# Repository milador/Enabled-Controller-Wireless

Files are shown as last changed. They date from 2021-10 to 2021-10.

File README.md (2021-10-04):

# Enabled-Controller-Wireless
Enabled Controller Wireless is an open-source bluetooth-enabled switch interface that enables those with limited or no hand movement to be able to use Adaptive switches and analog joysticks as inputs to operate their computers, smartphones, and game consoles.

<p align="center">
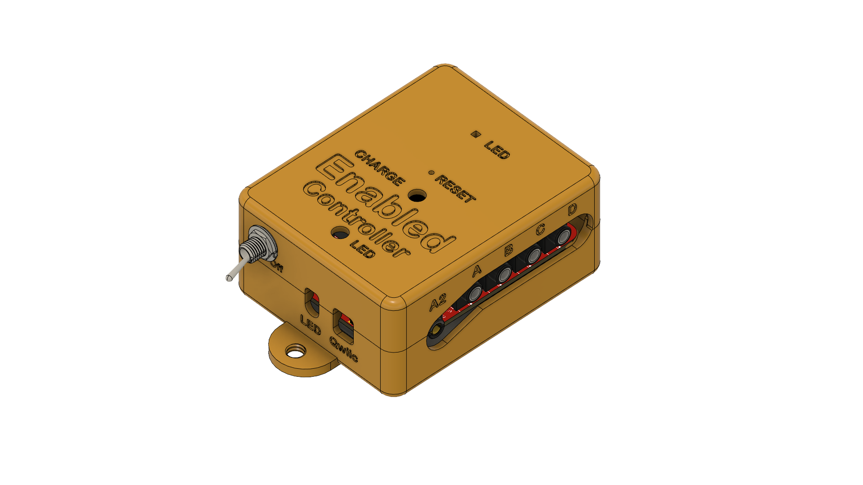
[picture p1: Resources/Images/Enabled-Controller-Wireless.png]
Enabled Controller Wireless

</p>

The device offers up to eight switch input enclosures through eight 3.5mm audio jacks and four analog inputs through two 3.5mm headphone jacks. The two 3.5mm headphone jacks can be used to connect up to two X-Y analog joysticks.

The internal RGB led of ItsyBitsy and external NeoPixel is used to provide visual feedback for each action.

## Assembly Instructions Manual

The <a href="https://github.com/milador/Enabled-Controller-Wireless/blob/master/Documentation/Build_Manuals/Enabled_Controller_Wireless_Instructions_Manual.pdf">Assembly Instructions Manual</a> is available to download.

## User Manual

### Enabled Controller Wireless User Manual

<a href="https://github.com/milador/Enabled-Controller-Wireless/blob/master/Documentation/User_Manuals/Enabled_Controller_Wireless_User_Manual.pdf">Enabled_Controller_Wireless_User_Manual.pdf</a>

## Parts

The <a href="https://github.com/milador/Enabled-Controller-Wireless/blob/master/Components/Enabled_Controller_Wireless_BOM.csv">BOM</a> file is available to download.

## Software

### Enabled_Controller_Wireless_Software.ino  

The <a href="https://raw.githubusercontent.com/milador/Enabled-Controller-Wireless/master/Software/Arduino/Enabled_Controller_Wireless_Software/Enabled_Controller_Wireless_Software.ino">Enabled_Controller_Wireless_Software.ino</a> allows you to use adaptive switches as input method via keyboard/mouse HID profiles. 

## Hardware 

### PCB Design 

The <a href="https://github.com/milador/Enabled-Controller-Wireless/tree/master/Hardware/PCB">PCB files</a> including both PCB Eagle design files and generated gerber files are available to download.

Front PCB:
<p align="center">
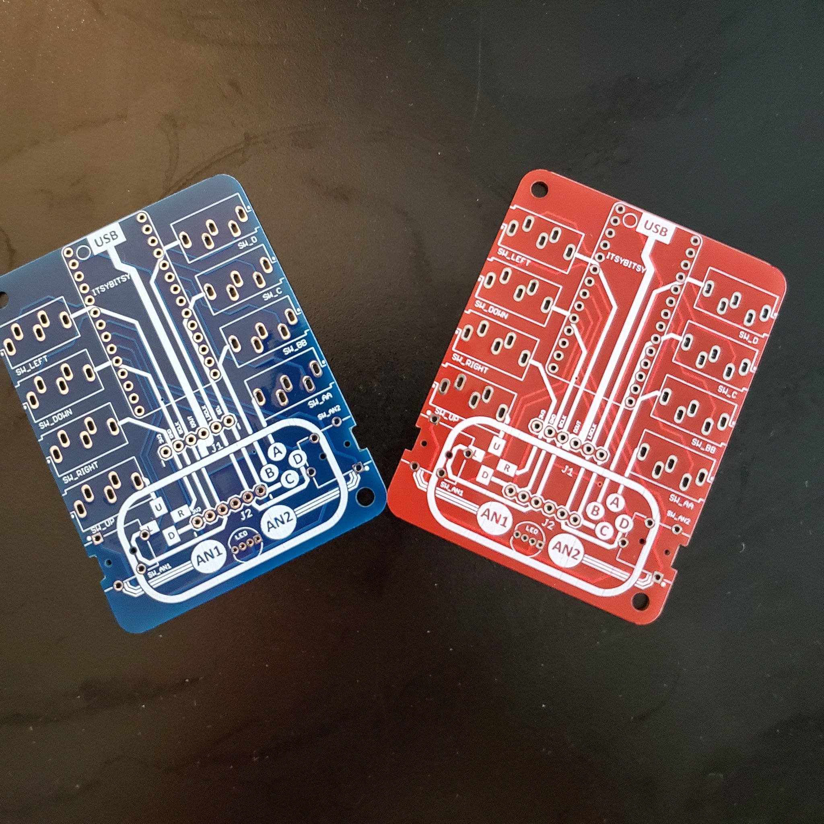
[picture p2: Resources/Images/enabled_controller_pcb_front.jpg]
Front PCB

</p>

Back PCB:
<p align="center">
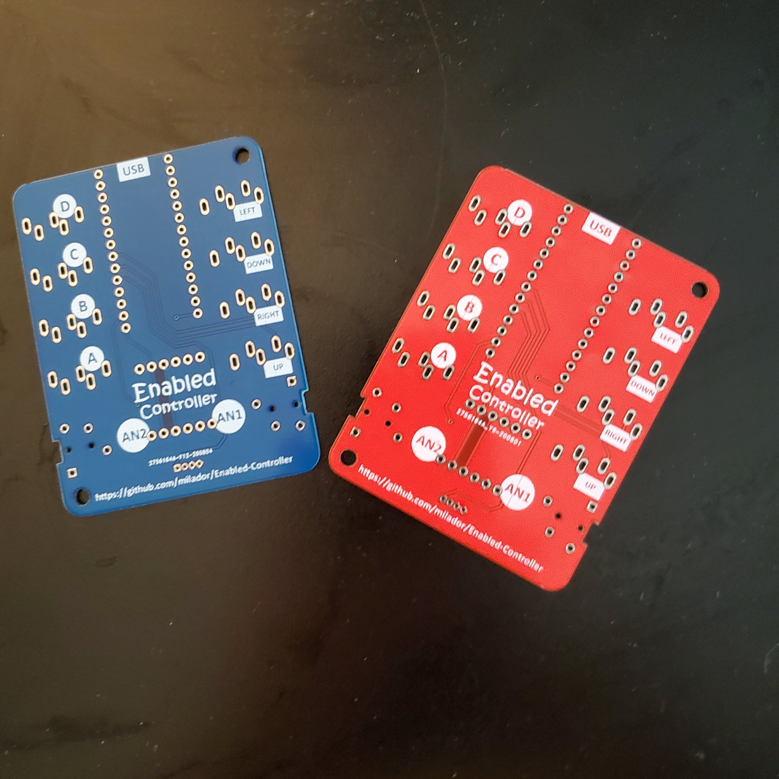
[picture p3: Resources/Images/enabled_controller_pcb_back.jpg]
Back PCB

</p>

Assembled:
<p align="center">
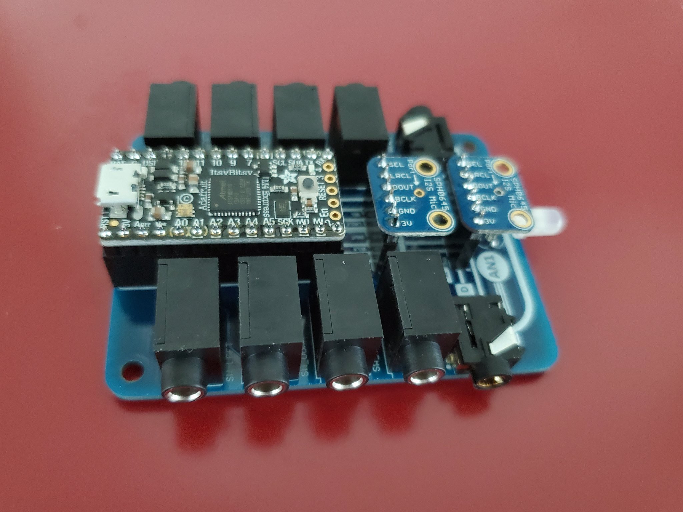
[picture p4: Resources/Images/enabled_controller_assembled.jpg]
Assembled PCB

</p>

Assembly Animation:

https://www.youtube.com/watch?v=7AMCL-cITrQ

### Enclosure

The <a href="https://github.com/milador/Enabled-Controller-Wireless/tree/master/Hardware/Enclosure">Enclosure files</a> including both STL and STEP enclosure files are available to download.

<p align="center">
Enabled Controller Wireless
</p>

## License

### Creative Commons Attribution-NonCommercial-ShareAlike (CC-BY-NC-SA)

Copyright (c) 2021 Milador

A creative commons license that bans commercial use and requires you to release any modified works under this license.

<p align="center">
CC-BY-NC-SA
</p>

<br />This work is licensed under a <a rel="license" href="http://creativecommons.org/licenses/by-nc-sa/3.0/">Creative Commons Attribution-NonCommercial-ShareAlike 3.0 Unported License</a>.

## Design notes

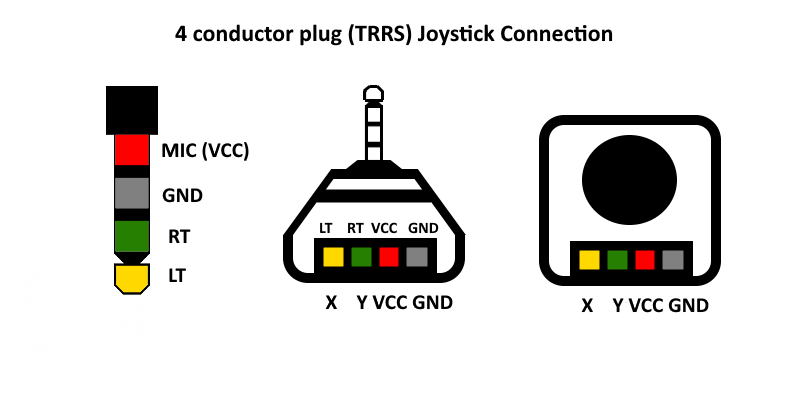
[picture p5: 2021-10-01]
Resources/Images/TRRS_Joystick_Mapping.png

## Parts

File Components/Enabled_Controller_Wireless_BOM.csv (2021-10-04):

Index | Quantity | Digikey Part Number | Manufacturer Part Number | Description | Price (CAD) | Unit Price (CAD) | Link
1 | 1 | 1528-4481-ND | 4481 | ITSYBITSY NRF52840 EXPRESS BLE | 26.96 | 26.96 | https://www.digikey.ca/en/products/detail/adafruit-industries-llc/4481/11497502
2 | 1 | 1568-1213-ND | COM-12986 | ADDRESS LED DISC SER RGB 5MM 5PC | 3.99 | 3.99 | https://www.digikey.ca/en/products/detail/COM-12986/1568-1213-ND/5673799
3 | 2 | S7047-ND | PPPC141LFBN-RC | CONN HDR 14POS 0.1 GOLD | 1.28 | 1.28 | https://www.digikey.ca/en/products/detail/PPPC141LFBN-RC/S7047-ND/810186
4 | 8 | CP1-3535NG-ND | SJ1-3535NG | CONN JACK STEREO 3.5MM R/A | 1.61 | 1.61 | https://www.digikey.ca/product-detail/en/cui-inc/SJ1-3535NG/CP1-3535NG-ND
5 | 2 | CP-43514-ND | SJ-43514 | CONN JACK 4COND 3.5MM | 1.43 | 1.43 | https://www.digikey.ca/en/products/detail/SJ-43514/CP-43514-ND/368146
6 | 2 | 36-4708-ND | 4708 | HEX NUT 0.217" STEEL M3 | 0.23 | 0.23 | https://www.digikey.ca/en/products/detail/keystone-electronics/4708/4499301
7 | 2 | 335-1148-ND | RM3X10MM 2701 | MACH SCREW PAN HEAD PHILLIPS M3 | 0.92 | 0.92 | https://www.digikey.ca/en/products/detail/apm-hexseal/RM3X10MM-2701/3712296
8 | 1 | PRT-14417-ND | PRT-14417 | QWIIC JST CONNECTOR - SMD 4-PIN | 0.68 | 0.68 | https://www.digikey.ca/en/products/detail/sparkfun-electronics/PRT-14417/7652746
9 | 1 | 1528-1443-ND | 2124 | PRO TRINKET LI-BATTERY BACKPACK | 6.69 | 6.69 | https://www.digikey.ca/en/products/detail/adafruit-industries-llc/2124/5761211
10 | 1 | S7036-ND | PPPC031LFBN-RC | CONN HDR 3POS 0.1 GOLD PCB | 0.5 | 0.5 | https://www.digikey.ca/en/products/detail/sullins-connector-solutions/PPPC031LFBN-RC/810175
11 | 1 | 1528-1841-ND | 1578 | BATTERY LITHIUM 3.7V 500MAH | 13.99 | 13.99 | https://elmwoodelectronics.ca/collections/adafruit/products/lithium-ion-polymer-battery-3-7v-500mah
12 | 1 | 2449-ANT13SEBQE-ND | ANT13SEBQE | SWITCH TOGGLE SPDT | 2.45 | 2.45 | https://www.digikey.ca/en/products/detail/cit-relay-and-switch/ANT13SEBQE/12503275
13 | 1 | 81044/12-24-6-DS-ND | 81044/12-24-6 | 81044/12-24-6 FEET HOOK-UP WIRE | 0.98 | 0.98 | https://www.digikey.ca/en/products/detail/te-connectivity-aerospace,-defense-and-marine/81044%2F12-24-6/6071077
 |  |  |  |  | Total Price (CAD) | 76.84
 |  | *Items 12 & 13 are optional

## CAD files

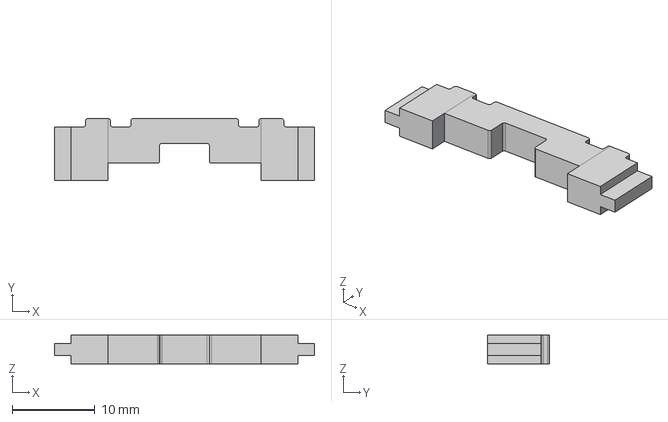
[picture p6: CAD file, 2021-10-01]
Hardware/Enclosure/STEP/Enabled_Controller_Wireless_Battery_Wall.step
31.5 x 7.50 x 3.50 mm

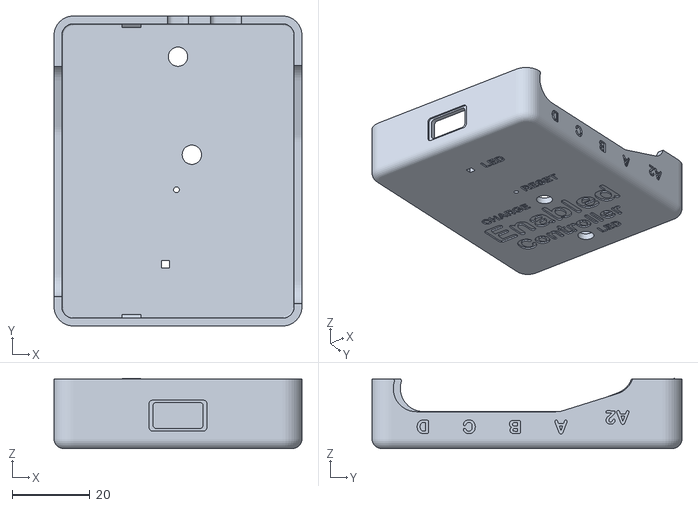
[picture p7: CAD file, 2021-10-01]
Hardware/Enclosure/STL/Enabled_Controller_Wireless_Top.stl
64.0 x 80.0 x 18.1

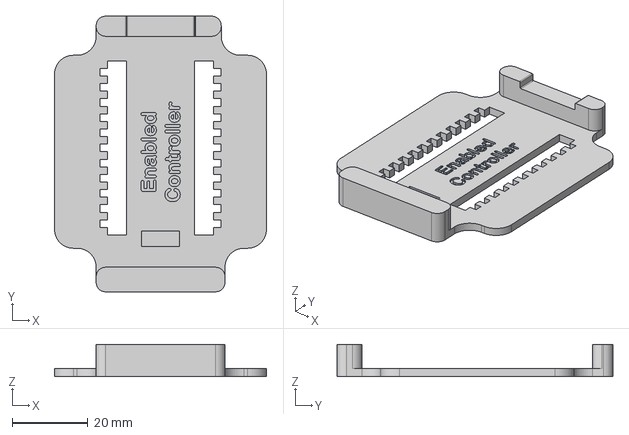
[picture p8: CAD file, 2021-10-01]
Hardware/Enclosure/STEP/Enabled_Controller_Wireless_Battery_Holder.step
56.0 x 72.8 x 8.50 mm

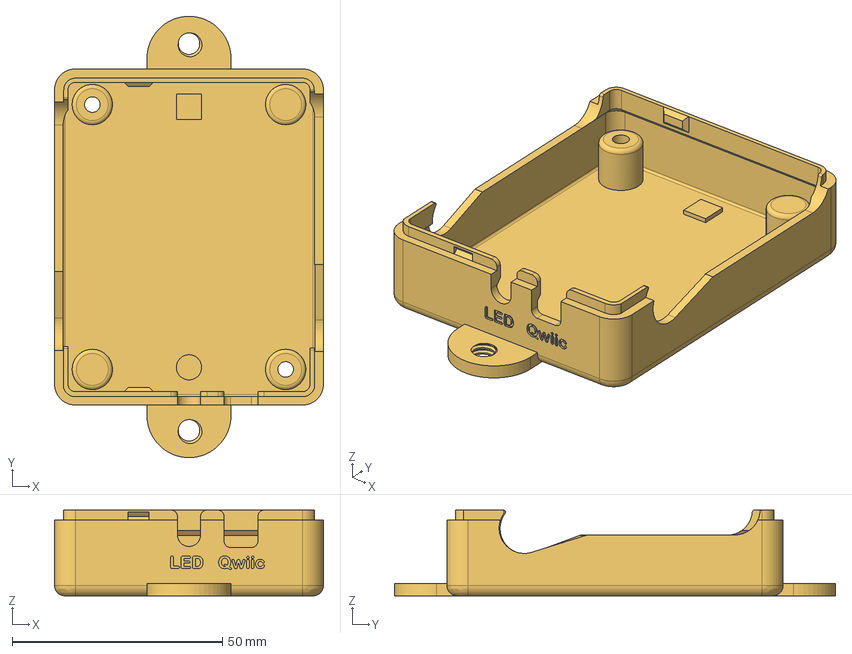
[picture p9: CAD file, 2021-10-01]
Hardware/Enclosure/STEP/Enabled_Controller_Wireless_Bottom_With_Mount.step
64.0 x 105.0 x 20.4 mm

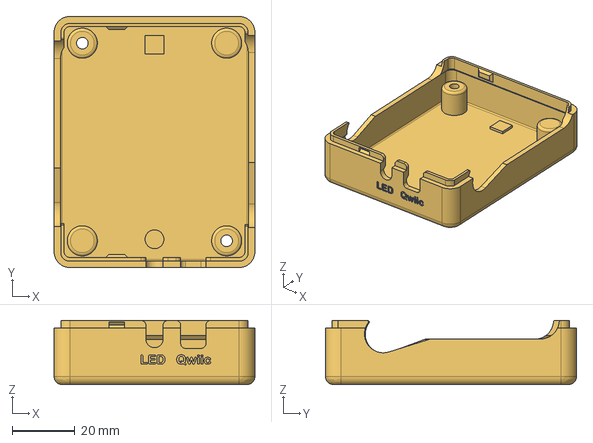
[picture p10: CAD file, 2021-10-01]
Hardware/Enclosure/STEP/Enabled_Controller_Wireless_Bottom.step
64.0 x 80.0 x 20.4 mm

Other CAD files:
Hardware/Enclosure/STL/Enabled_Controller_Wireless_Battery_Holder.stl
Hardware/Enclosure/STL/Enabled_Controller_Wireless_Battery_Wall.stl
Hardware/Enclosure/STL/Enabled_Controller_Wireless_Bottom.stl
Hardware/Enclosure/STL/Enabled_Controller_Wireless_Bottom_With_Mount.stl

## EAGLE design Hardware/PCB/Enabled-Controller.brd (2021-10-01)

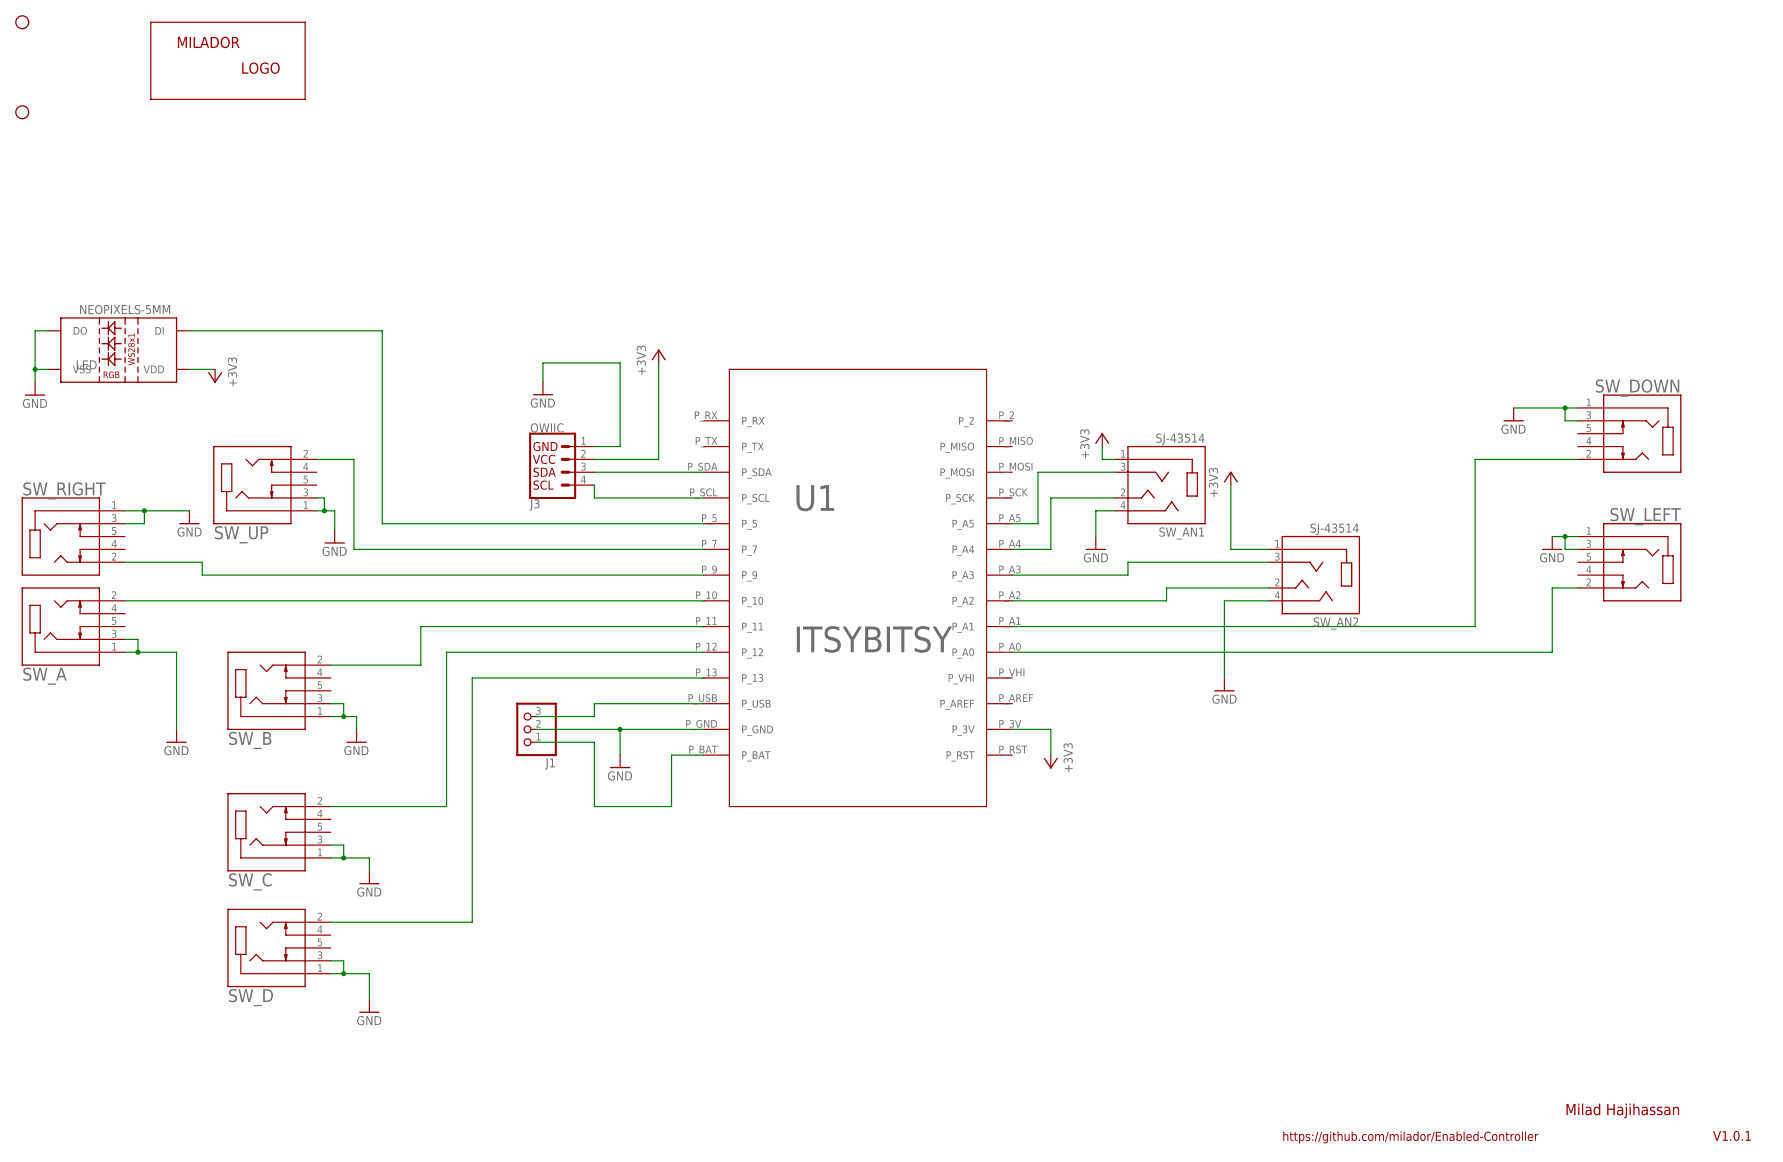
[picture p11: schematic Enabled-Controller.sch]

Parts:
J1: HEADER_FEMALE-1X3-LONGER; HEADER_FEMALE-1X03_LONGER
J3: QWIIC; CONNECTORS_JST04_1MM_RA
LABEL1: MILADOR-LOGO-; MILADOR_LOGO1
LED: NEOPIXELS-5MM
STANDOFF1, STANDOFF2: STAND-OFF-; STAND-OFF
SW_A: CUI_SJ1-3535NGSJ1-3535NG; CUI_SJ1-3535NG
SW_AN1, SW_AN2: SJ-43514; CUI_SJ-43514
SW_B: CUI_SJ1-3535NGSJ1-3535NG; CUI_SJ1-3535NG
SW_C: CUI_SJ1-3535NGSJ1-3535NG; CUI_SJ1-3535NG
SW_D: CUI_SJ1-3535NGSJ1-3535NG; CUI_SJ1-3535NG
SW_DOWN: CUI_SJ1-3535NGSJ1-3535NG; CUI_SJ1-3535NG
SW_LEFT: CUI_SJ1-3535NGSJ1-3535NG; CUI_SJ1-3535NG
SW_RIGHT: CUI_SJ1-3535NGSJ1-3535NG; CUI_SJ1-3535NG
SW_UP: CUI_SJ1-3535NGSJ1-3535NG; CUI_SJ1-3535NG
U1: ITSYBITSY; ITSYBITSY-V2

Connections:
+3V3: J3.2, LED.P2 (VDD), SW_AN1.1 (SLEEVE), SW_AN2.1 (SLEEVE), U1.P_3V
GND: J1.2, J3.1, LED.P3 (VSS), LED.P4 (DO), SW_A.1, SW_A.3, SW_AN1.4 (RING2), SW_AN2.4 (RING2), SW_B.1, SW_B.3, SW_C.1, SW_C.3, SW_D.1, SW_D.3, SW_DOWN.1, SW_DOWN.3, SW_LEFT.1, SW_LEFT.3, SW_RIGHT.1, SW_RIGHT.3, SW_UP.1, SW_UP.3, U1.P_GND
unnamed: SW_D.2, U1.P_13
unnamed: SW_C.2, U1.P_12
unnamed: SW_B.2, U1.P_11
unnamed: SW_AN1.2 (TIP), U1.P_A4
unnamed: SW_DOWN.2, U1.P_A1
unnamed: SW_RIGHT.2, U1.P_9
unnamed: SW_UP.2, U1.P_7
unnamed: SW_AN1.3 (RING1), U1.P_A5
unnamed: SW_AN2.3 (RING1), U1.P_A3
unnamed: SW_A.2, U1.P_10
unnamed: SW_LEFT.2, U1.P_A0
unnamed: SW_AN2.2 (TIP), U1.P_A2
unnamed: LED.P1 (DI), U1.P_5
unnamed: J3.4, U1.P_SCL
unnamed: J3.3, U1.P_SDA
unnamed: J1.3, U1.P_USB
unnamed: J1.1, U1.P_BAT

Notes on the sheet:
V1.0.1
Milad Hajihassan
https://github.com/milador/Enabled-Controller

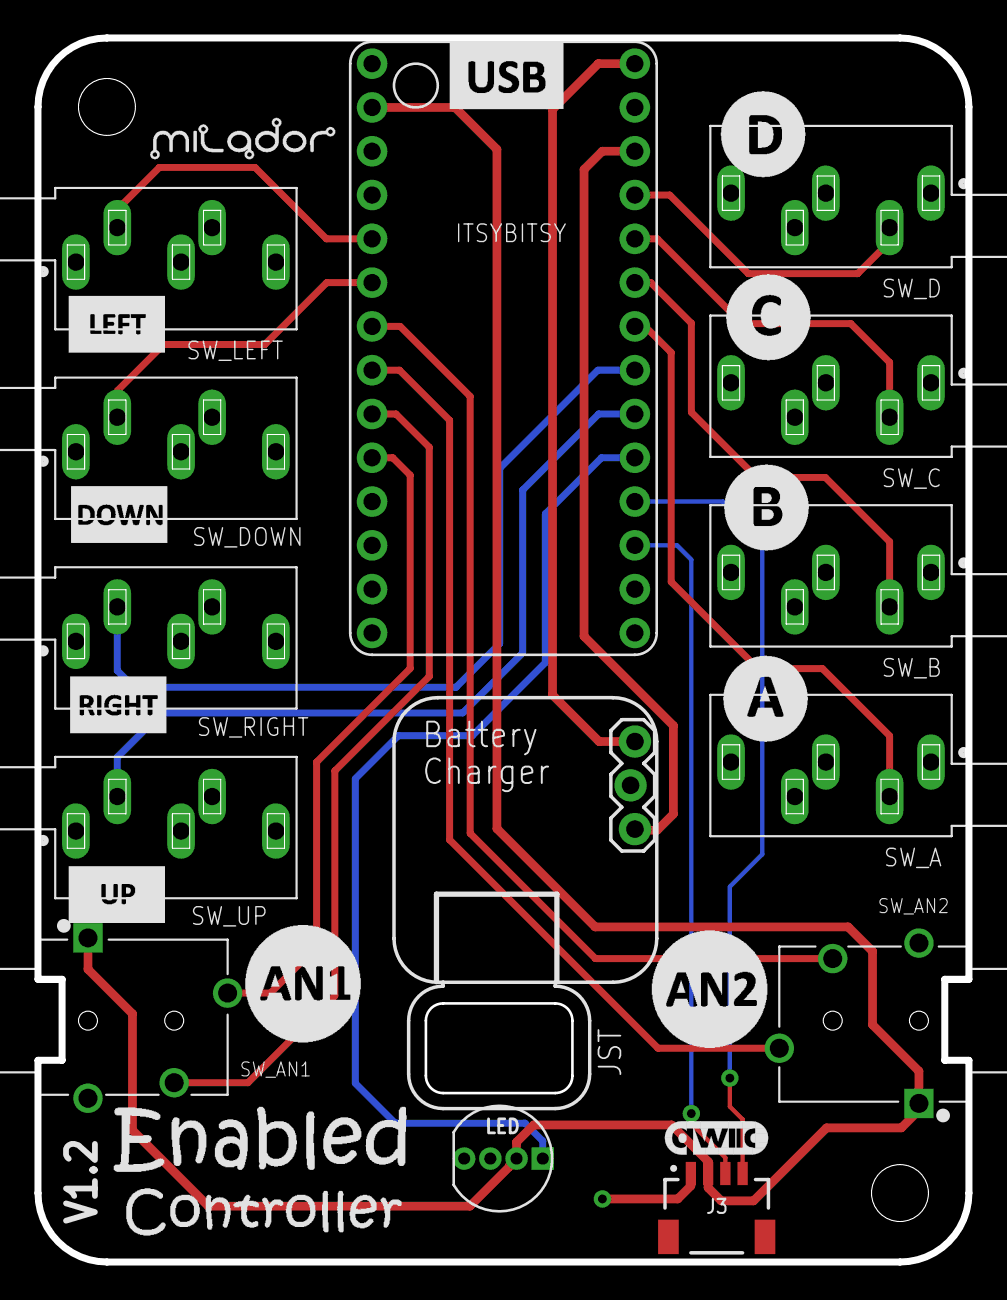
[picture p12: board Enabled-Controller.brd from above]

Board: 2 copper layers, 54.0 x 71.0 mm, 18 parts (0 on the bottom side), 19 nets.

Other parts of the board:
LABEL2: QWIIC_6MM

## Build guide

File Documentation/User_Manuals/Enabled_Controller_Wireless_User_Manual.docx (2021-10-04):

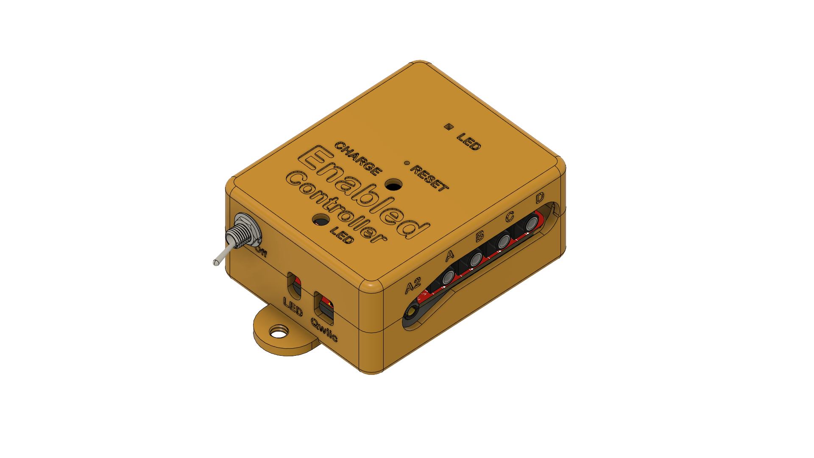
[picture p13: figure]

Enabled Controller Wireless User Manual | An accessible adaptive switch interface box Version 1.2 https://github.com/milador/Enabled-Controller-Wireless

# Usage

The Enabled Controller Wireless can be used in different configurations based on the needs of the end user. The Enabled Controller hardware can be used along different software as input device for multiple devices. The hardware allows you connect up to eight input 3.5mm adaptive switches which are marked A,B,C,D,UP,RIGHT,DOWN,LEFT on both circuit board and the enclosure.

All four switches can be used as inputs when short pressed and switch D can be used to change the operation mode when it’s pressed and hold for more than 2 seconds. Table 1 represents all the possible actions for switches and their corresponding led feedback.

Button | Action | Color
A | Short press | Blue
B | Short press | Red
C | Short press | Green
D | Short press | Yellow
D | Long Press | Mode Led Color
UP | Short press | Yellow
RIGHT | Short press | Yellow
DOWN | Short press | Yellow
LEFT | Short press | Yellow

Table 1: Enabled Controller Wireless switch actions and feedback

The device will blink two times in the color of operating mode when the initialization process is completed and will stay in that color. The led will blink momentary in color of the switch pressed as represented in Table 1 and the led color will go back to the color of operating mode. The mode can only change when switch D is pressed and hold for 2 seconds.

The WIRELESS version is great for usage along computer or smartphone devices as it’s able to simulate a Bluetooth mouse or Bluetooth keyboard device. The Wireless version can operate in different modes as it’s represented in Table 2.

Mode Number | Mode | Color
1 | Keyboard Switch | Teal
2 | Morse Keyboard | Purple
3 | Morse Mouse | Pink
4 | Mouse | Green
5 | Settings | Orange

Table 2: Enabled Controller Wireless modes

### Keyboard Switch mode

The Keyboard Switch will operate similar to a four key keyboard which is great for using as switches for your computer or smartphone device through features such as Switch access and it can also be used to play computer games via WASD format keyboard.

The switch mode does not work the exact same way in all the Operating Systems and as the results, you may need to modify the keystrokes sent for each switch.

Enabled-Controller has two OS profile options which you can select from depending on the Operating System of your host device.

#### OS PROFILE #1: Windows and Android

Button | Action | Color | Result
A | Short press | Blue | Send ‘a’ keystroke
B | Short press | Red | Send ‘b’ keystroke
C | Short press | Green | Send ‘c’ keystroke
D | Short press | Yellow | Send ‘d’ keystroke
D | Long Press | Mode Led Color | Change operating mode
UP | Short press | Yellow | Send KEY_UP_ARROW keystroke
RIGHT | Short press | Yellow | Send KEY_RIGHT_ARROW keystroke
DOWN | Short press | Yellow | Send KEY_DOWN_ARROW keystroke
LEFT | Short press | Yellow | Send KEY_LEFT_ARROW keystroke

Table 3: Enabled Controller Wireless switch actions (OS PROFILE #1)

#### OS PROFILE #2: macOS

Button | Action | Color | Result
A | Short press | Blue | Send KEY_F1 keystroke
B | Short press | Red | Send KEY_F2 keystroke
C | Short press | Green | Send KEY_F3 keystroke
D | Short press | Yellow | Send KEY_F4 keystroke
D | Long Press | Mode Led Color | Change operating mode
UP | Short press | Yellow | Send KEY_F5 keystroke
RIGHT | Short press | Yellow | Send KEY_F6 keystroke
DOWN | Short press | Yellow | Send KEY_F7 keystroke
LEFT | Short press | Yellow | Send KEY_F8 keystroke

Table 4: Enabled Controller Wireless switch actions (OS PROFILE #2)

The time between each switch press actions is calculated by switch reaction levels which can be changed in settings mode or manually through the software. The switch reaction time variable is used to calculate the reaction time for each of the 10 levels as represented in Table 5.

SWITCH_REACTION_TIME 50

The switch reaction time variable is set to 50 by default.

Level | 10 | 9 | 8 | 7 | 6 | 5 | 4 | 3 | 2 | 1
Time (ms) | 1*50 | 2*50 | 3*50 | 4*50 | 5*50 | 6*50 | 7*50 | 8*50 | 9*50 | 10*50

Table 5: Enabled Controller Wireless switch reaction time

### Morse Keyboard Mode

This mode is used to convert morse code to keystrokes via 2 switches. The first switch acts as dot and second switch acts as dash as explained in Table 6.

Button | Action | Color | Result
A | Short press | Blue | Send ‘.’ To morse stack
B | Short press | Red | Send ‘-’ To morse stack
D | Long Press | Mode Led Color | Change operating mode

Table 6: Enabled Controller Wireless morse keyboard mode

The conversion of morse code combination to characters is done in software based on the static variables in the beginning of the code. These values can be customized based on your needs.

MORSE_TIMEOUT 1000

MORSE_REACTION_TIME 10

The timeout is the time in ms that is measured since last switch action to perform the morse conversation and send the result as keystroke. The time by default is set to 1 second ( 1000 ms ) which means the device will convert the morse code combinations if switch A and B (Dot , Dash ) are not pressed for 1 second.

The reaction time is the multiplier for time between each dot and dash. The higher reaction level means lower reaction time. The reaction levels can be changed using switches in the settings mode but it’s also possible to change the morse reaction time multiplier in the code. Table 7 can be used to understand the morse reaction time calculation.

Level | 10 | 9 | 8 | 7 | 6 | 5 | 4 | 3 | 2 | 1
Time (ms) | (1.5^1)*10 | (1.5^2)*10 | (1.5^3)*10 | (1.5^4)*10 | (1.5^5)*10 | (1.5^6)*10 | (1.5^7)*10 | (1.5^8)*10 | (1.5^9)*10 | (1.5^10)*10

Table 7: Enabled Controller Wireless morse reaction time

The table of morse code combinations can be found on EasyMorseBlue (https://github.com/milador/EasyMorseBlue) project github repository.

### Morse Mouse Mode

This mode is used to convert morse code to mouse actions via 2 switches. The first switch acts as dot and second switch acts as dash as explained in Table 8.

Button | Action | Color | Result
A | Short press | Blue | Send ‘.’ To morse stack
B | Short press | Red | Send ‘-’ To morse stack
D | Long Press | Mode Led Color | Change operating mode

Table 8: Enabled Controller Wireless morse mouse mode

This mode users the morse timeout value and morse reaction time to convert morse code combinations to mouse actions similar to morse keyboard mode. The table of morse code combinations can be found on EasyMorseBlue (https://github.com/milador/EasyMorseBlue) project github repository. The conversion table is represented in Table 9 in addition.

Morse code | Result
- | Move Up
-- | Move Down
.. | Move Left
... | Move Right
.- | Left Click
.-- | Right Click
..- | Double Left Click
..-- | Double Right Click
-. | Left Click & Hold/Release
-.. | Right Click & Hold/Release

Table 9: Enabled Controller Wireless morse mouse code conversion table

The mouse move actions are fixed in terms of number of pixels that cursor can be moved for each morse code combination, but there is mouse move multiplier variable available in the software that allows you to customize the mouse move behavior based on your needs.

MOUSE_MOVE_MULTI 2

The mouse move multiplier variable is set to 2 by default.

### Mouse Mode

This mode is used to simulate a mouse device using the dual analog joysticks and input switches.

Button | Action | Color | Result
A | Short press | Blue | Left Click
B | Short press | Red | Right Click
C | Short press | Green | No Action
D | Short press | Yellow | No Action
D | Long Press | Mode Led Color | Change operating mode
Up | Short press | Yellow | No Action
Right | Short press | Yellow | No Action
Down | Short press | Yellow | No Action
Left | Short press | Yellow | No Action

Table 10: Enabled Controller Wireless mouse mode switch actions

Action | Color | Result
Joystick X1 | Yellow | Move Cursor Left or Right
Joystick Y1 | Yellow | Move Cursor Up or Down
Joystick X2 | Yellow | Move Cursor Left or Right
Joystick Y2 | Yellow | Move Cursor Up or Down

Table 11: Enabled Controller Wireless mouse mode joystick actions

The user has option to enable and select the analog joystick port number using constants defined in the firmware.

JOYSTICK_ENABLED false

JOYSTICK_NUMBER 2

There is an option to select the desired dead zone value based on the user ability and needs.

JOYSTICK_DEADZONE 20

### Settings Mode

The settings mode is used to change the reaction level and reaction time using the A and B switches. The led will blink in blue when react level is increased and in red when reaction level is decreased. The number of led blinks indicate new reaction level. The led will blink 10 times when it reaches maximum or minimum reaction levels.

Button | Action | Color | Result
A | Short press | Blue | Increase Reaction level (Decrease Reaction time)
B | Short press | Red | Decrease Reaction level (Increase Reaction time)
D | Long Press | Mode Led Color | Change operating mode

Table 12: Enabled Controller Wireless settings mode

There are total of 10 levels and the switch reaction times and morse reaction times can be calculated using Tablets 11 and 12.

Level | 10 | 9 | 8 | 7 | 6 | 5 | 4 | 3 | 2 | 1
Time (ms) | 1*50 | 2*50 | 3*50 | 4*50 | 5*50 | 6*50 | 7*50 | 8*50 | 9*50 | 10*50

Table 13: Enabled Controller Wireless switch reaction time

Level | 10 | 9 | 8 | 7 | 6 | 5 | 4 | 3 | 2 | 1
Time (ms) | (1.5^1)*10 | (1.5^2)*10 | (1.5^3)*10 | (1.5^4)*10 | (1.5^5)*10 | (1.5^6)*10 | (1.5^7)*10 | (1.5^8)*10 | (1.5^9)*10 | (1.5^10)*10

Table 14: Enabled Controller Wireless morse reaction time

## Customization

The Enabled Controller Wireless can easily be customized by changing the value of variables at the beginning of Enabled Controller Wireless software. The following variables can be changed for customization purposes:

#define SWITCH_MAC_PROFILE false

This variable is created to set the keys to be used as switches based on host device OS profile (Windows & Android = false , macOS = true )

#define MORSE_TIMEOUT 1000

The time of no activity which is used as flag to convert the morse combination to keystroke

#define MORSE_REACTION_TIME 10

The morse reaction time multiplier between each dot and dash actions

#define MOUSE_MOVE_MULTI 2

The morse mouse move multiplier variable

#define SWITCH_REACTION_TIME 50

The switch reaction time multiplier between each switch action

#define SWITCH_MODE_CHANGE_TIME 2000

The time that switch D needs to be hold in ms to perform mode change action

#define LED_BRIGHTNESS 150

The brightness of led for mode indication

#define LED_ACTION_BRIGHTNESS 150

The brightness of led for action indication

//Switch properties

const switchStruct switchProperty[] {

{1,"DOT",HID_KEY_A,HID_KEY_F1,MOUSE_LEFT_CLICK,5,1}, //{1=dot,"DOT",'a','F1',5=blue,1=1xMORSE_REACTION}

{2,"DASH",HID_KEY_B,HID_KEY_F2,MOUSE_RIGHT_CLICK,6,3}, //{2=dash,"DASH",'b','F2',6=red,3=3xMORSE_REACTION}

{3,"C",HID_KEY_C,HID_KEY_F3,MOUSE_DOUBLE_LEFT_CLICK,1,1}, //{3,"C",'c','F3',1=green,1=1xMORSE_REACTION}

{4,"D",HID_KEY_D,HID_KEY_F4,MOUSE_DOUBLE_RIGHT_CLICK,3,1}, //{4,"D",'d','F4',3=yellow,1=1xMORSE_REACTION}

{5,"UP",HID_KEY_ARROW_UP,HID_KEY_F5,MOUSE_NO_ACTION,4,1}, //{5,"UP",'UP','F5',4=orange,1=1xMORSE_REACTION}

{6,"RIGHT",HID_KEY_ARROW_RIGHT,HID_KEY_F6,MOUSE_NO_ACTION,4,1}, //{6,"RIGHT",'RIGHT','F6',4=orange,1=1xMORSE_REACTION}

{7,"DOWN",HID_KEY_ARROW_DOWN,HID_KEY_F7,MOUSE_NO_ACTION,4,1}, //{7,"DOWN",'DOWN','F7',4=orange,1=1xMORSE_REACTION}

{8,"LEFT",HID_KEY_ARROW_LEFT,HID_KEY_F8,MOUSE_NO_ACTION,4,1}, //{8,"LEFT",'LEFT','F8',4=orange,1=1xMORSE_REACTION}

{9,"ANALOG",HID_KEY_NONE,HID_KEY_NONE,MOUSE_NO_ACTION,4,1} //{9,"ANALOG",'NONE','F9',4=orange,1=1xMORSE_REACTION}};

The values of third column can be changed to different characters and the fourth column can be changed for customization of led feedback.

//Settings Action properties

const settingsActionStruct settingsProperty[] {

{1,"Increase Reaction",5}, //{1=Increase Reaction,5=blue}

{2,"Decrease Reaction",6}, //{2=Decrease Reaction,6=red}

{3,"Max Reaction",1}, //{3=Max Reaction,1=green}

{4,"Min Reaction",1} //{4=Min Reaction,1=green}

};

The third column can be changed for customization of led feedback.

//Mode properties

const modeStruct modeProperty[] {

{1,"Keyboard Switch",8},

{2,"Morse Keyboard",7},

{3,"Morse Mouse",2},

{4,"Mouse",1},

{5,"Settings",4}

};

The third column can be changed for customization of led feedback.

const colorStruct colorProperty[] {

{1,"Green",{0,50,0}},

{2,"Pink",{50,00,20}},

{3,"Yellow",{50,50,0}},

{4,"Orange",{50,20,0}},

{5,"Blue",{0,0,50}},

{6,"Red",{50,0,0}},

{7,"Purple",{50,0,50}},

{8,"Teal",{0,128,128}}

};

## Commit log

2021-10-01 Added version 1.2
    [Enabled-Controller.brd, Enabled-Controller.sch, Enabled_Controller_Wireless_BOM.csv, Enabled_Controller_Wireless_BOM.xlsx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]
2021-10-01 Added PCB Images
2021-10-04 Added additional information to the documentation
    [Enabled_Controller_Wireless_BOM.csv, Enabled_Controller_Wireless_BOM.xlsx]

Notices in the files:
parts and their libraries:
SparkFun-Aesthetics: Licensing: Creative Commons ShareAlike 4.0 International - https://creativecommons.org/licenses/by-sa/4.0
